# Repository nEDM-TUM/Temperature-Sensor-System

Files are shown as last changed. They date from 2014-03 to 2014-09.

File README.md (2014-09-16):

Temperature-Sensor-System
==============

Sensor network system built for the nEDM experiment.

Features
------------------
- Both temperature and humidity sensors can be connected at any sensor socket.
The sensor type will be automatically detected.
- High temperature and humidity accuracy: Temperature sensors are calibrated to ±0.1K and the humidity sensors to ±1.8%rH.
- A high number of connected sensors is supported. Currently 44 sensors are in use, however the system is designed to support at least 100 sensors and still be able to fulfill a sampling rate of 1Hz. If the sampling rate is allowed to be slower, up to 960 sensors are possible to share one Ethernet connection.
- The system supports a fast sample rate of at least 1Hz.
- We achieved a relatively low cost per sensor. The cost per sensor module is mostly defined by the sensor chip alone, which is about e7 for a precision temperature sensor and about e20 for a high quality humidity sensor. The cost for the printed circuit board and required components is less than e4 per board.
- Measurement results can be forwarded via TCP/IP to a CouchDB server, which is able to record the measurement data from all connected sensors.
- The sensor network provides a TCP/telnet user interface, for controlling and viewing of network parameters. This allows easy configuring and debugging of the system.
- Most of the system parameters like sampling rate or database IP addresses and insert functions are configurable at runtime.
- Plug and Play is supported for adding and removing sensors or even control units during runtime.

Directory structure
--------------------
```
.
+-- casings     // 3D CAD files for 3D printer
|   +-- adapter
|   +-- arduino
|   +-- cable_clamp
|   +-- collector
|   +-- humidity
|   +-- temperature
+-- circuit_boards      // Circuit schematic diagram and 
|   |                   // PCB schematic files created using KiCad
|   +-- 3x127_254_adapter       // A PCB chip adapter, 
|   |                           // used for breadboard debugging
|   +-- 4x127_254_adapter       // A PCB chip adapter, 
|   |                           // used for breadboard debugging
|   +-- arduino_adapter
|   +-- humidity
|   +-- kicad_library           // Footprint and Component
|   |                           // library files for KiCad
|   +-- order           // PCB assembly, which was sent to 
|   |                   // Fischer Leiterplatten for production
|   +-- sensor_board
|   +-- so8_breakout    // A PCB chip adapter, 
|   |                   // used for breadboard debugging
|   +-- temperature_board
+-- datasheets      // Datasheets for sensors, micro processor, etc.
+-- presentation    // Slides (tex files) for a project presentation
+-- registration    
|   +-- description     // Project description (tex files) 
|                       // used for registration
+-- report      // Main project documentation (tex files)
+-- shop_orders // Receipts of orders from hardware shops
+-- sofware
|   +-- avr_wcet_analyzer   // code of a WCET analyzer
|   |                       // for the AVR instruction set
|   +-- collector_board      
|   +-- ethernet_board        
|   +-- humidity_board      
|   +-- util        // Commonly used utility code
+-- squid_analysis      
|   +-- data            // Squid magnetic field measurement protocol.
|                       // For squid data please write a mail to us.
|   +-- evaluation      // Evaluation script of squid analysis data
```

Tips for developers
--------------------
- To prevent EEPROM from being corrupted on power cycles, the AVR integrated brownout detection should be enabled.
- To allow EEPROM storage to stay intact after reprogramming, set the corresponding fuse bit.
- As Arduino fuses are not possible to be programmed via the default Arduino programmer (using the Arduino boot loader), we removed the boot loader and use the ISP connector for programming.
- To not overload the voltage regulator, especially when driving multiple boards one should consider, that a significant portion of power is used to drive LEDs. So turning the LEDs off during normal operation will prevent overheating.
- When debugging and programming devices of the sensor network, one has to be very careful, to not provide different power sources, as this might cause unexpected results, which can lead to damage of the sensor network, as well as connected computers. By default the USBasp programmer provides the system with 5V power.
- Our makefiles currently do not support automatic detection of file dependencies, and source files to be compiled. All source files have to be specified explicitly and if changes to header files are made, a ’make clean’ should be performed before compiling the program.
- Be careful, when using the USART line or similar for generating debugging output. Transmitting debugging information takes relatively long time and might influence the system heavily, especially, when debugging timing critical code. LEDs or GPIO pins with an oscilloscope provide a faster but more complex way for debugging.

###For more details about our project, please read the report document. ###
Its tex file and needed images can be found in the folder _report_. You can use _make_ to compile the document.

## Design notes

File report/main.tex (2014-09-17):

% Cover letter using letter.cls
\documentclass[a4paper]{scrreprt} 
%\usepackage{helvetica} % uses helvetica postscript font (download helvetica.sty)
%\usepackage{newcent}   % uses new century schoolbook postscript font 
\usepackage[utf8]{inputenc}
\usepackage[toc,page]{appendix}
\usepackage{graphicx}
\usepackage{amsmath}
\usepackage{eurosym}
\usepackage{cite}
\usepackage{tabularx}
\usepackage{bytefield}
\usepackage{color}
\usepackage{longtable}
\usepackage{tabularx}
\usepackage{url}
\usepackage[bookmarks]{hyperref}
\hypersetup{pdftex,colorlinks=true,allcolors=black}
\usepackage{hypcap}
\usepackage{listings}
\usepackage{color}
% the following commands control the margins:
%\topmargin=-1in    % Make letterhead start about 1 inch from top of page 
%\textheight=8.5in    % text height can be bigger for a longer letter
%\oddsidemargin=0pt   % leftmargin is 1 inch
%\textwidth=6.5in     % textwidth of 6.5in leaves 1 inch for right margin
\title{Implementing a temperature and humidity sensor network for the nEDM
experiment setup}
\author{Wenwen Chen, Rainer Schönberger}
\begin{document}
\maketitle
\tableofcontents
%###############################################################
\chapter{Introduction}
%%%%%%%%%%%%%%%%%%%%%%%%%%%%%%%%%%%%%%%%%%%%%%%%%%%%%%%%%%%%%%%
\section{Background}
\subsection{The neutron electric dipole measurement}
According to the standard model, it is assumed, that neutrons possess a electric dipole moment (EDM)
in the order of $10^{-32}e\cdot cm$. However an extension of the standard model already predicts
a dipole moment in the order between $10^{-26}e\cdot cm$ and $10^{-28}e\cdot cm$. Until now, no
experiment was able to do measurements more precise than $10^{-26}e\cdot cm$\cite{frmexp}.\\
The Neutron EDM (nEDM) experiment at Technische Universitat München is trying to increase the precision
of such a dipole moment measurement\cite{frmexp}.\\
The experiment uses spin polarized ultra cold neutrons, which are guided into two chambers inside a
highly controlled and magnetically shielded environment (see figure \ref{fig:exp}). There, a spin precession measurement according
to Ramsey \cite{ramsey} is performed, which allows it, to get information about the dipole moment of the neutrons.
\begin{figure}[h]
\centering
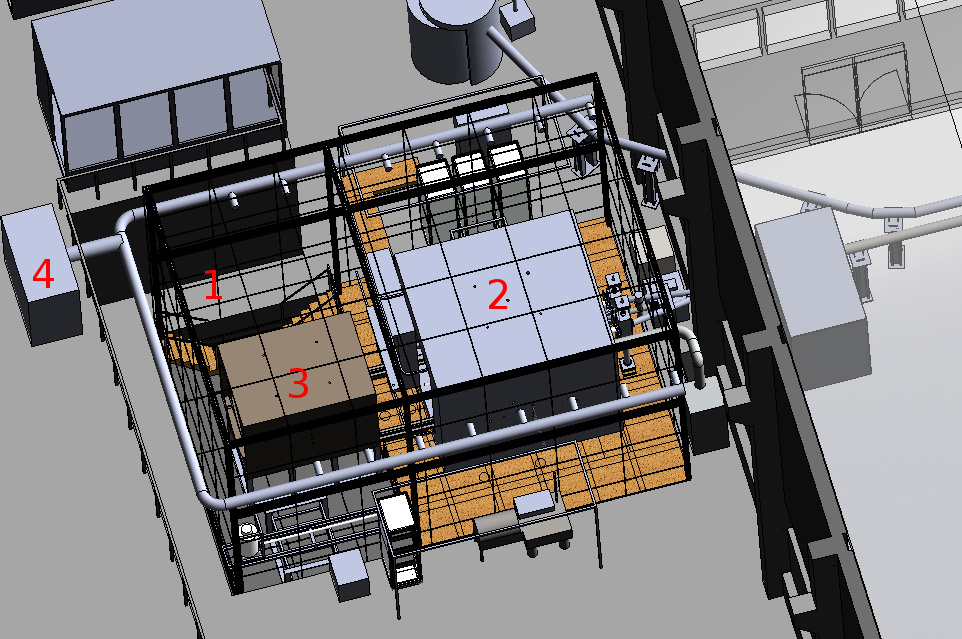
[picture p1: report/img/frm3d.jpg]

\caption{Experiment environment. 1: Field cage for magnetic field compensation, 2: Outer magnetic shield, 3: Inner magnetic shield, 4: Air conditioning system. Source: \cite{fiewiki}}
\label{fig:exp}
\end{figure}
\subsection{Temperature measurement}
Besides an exactly defined magnetic environment inside the experiment setup, a well defined
environment temperature and humidity is also important for the experiment. Therefore a
air conditioning system is installed to regulate the temperature inside the field cage.
Our temperature sensor network will provide data for the air conditioning system.\\
As a precise homogeneous temperature distribution inside the whole field cage is
almost impossible to achieve, our sensor network will provide precise temperature and humidity data. These data can be used to determine if specific physical observations are dependant
on temperature changes in the environment. Also a temperature compensation of measurements
based on environment temperature is possible.
%%%%%%%%%%%%%%%%%%%%%%%%%%%%%%%%%%%%%%%%%%%%%%%%%%%%%%%%%%%%%%%
\section{Features}
Our finished sensor network provides the following features:
\begin{itemize}
  \item Both temperature and humidity sensors can be connected at any
    sensor socket. The sensor type will be automatically detected.
  \item High temperature and humidity accuracy: Temperature sensors
    are calibrated to $\pm 0.1\,\mathrm{K}$ and the humidity
    sensors to $\pm 1.8\,\%\,\mathrm{rH}$.
  \item A high number of connected sensors is supported.
    Currently 44 sensors are in use, however the system is designed
    to support at least 100 sensors and still be able to fulfill a
    sampling rate of $1\,\mathrm{Hz}$. If the sampling rate is
    allowed to be slower, up to 960 sensors are possible to share
    one Ethernet connection.
  \item The system supports a fast sample rate of at least $1\,\mathrm{Hz}$.
  \item We achieved a relatively low cost per sensor. The cost per
    sensor module is mostly
    defined by the sensor chip alone, which is about \EUR{7} for a
    precision temperature sensor and about \EUR{20} for a high quality
    humidity sensor (also see section \ref{chap:sensors}). The cost for
    the printed circuit board and required components is less than
    \EUR{4} per board.
  \item Measurement results can be forwarded via TCP/IP to a CouchDB
    server, which is able to record the measurement data from all
    connected sensors.
  \item The sensor network provides a TCP/telnet user interface, for
    controlling and viewing of network parameters. This allows easy configuring
    and debugging of the system.
  \item Most of the system parameters like sampling rate or database IP addresses
    and insert functions are configurable at runtime.
  \item Plug and Play is supported for adding and removing sensors or even
    control units during runtime.
\end{itemize}
%###############################################################
\chapter{Technology}
%%%%%%%%%%%%%%%%%%%%%%%%%%%%%%%%%%%%%%%%%%%%%%%%%%%%%%%%%%%%%%%
\section{Sensors}\label{chap:sensors}
\subsection{TSIC 506F}
For temperature measurements, we use the TSIC 506F temperature sensor
integrated circuit chip. At a relatively low price of about \EUR{7} per device, it
is able to deliver very high accuracy (see table \ref{tab:tsic}).\\
The temperature is converted to a digital value, which is sent out over a
proprietary one wire protocol variant, called \emph{ZAC-Wire}. The transmission structure can be seen in figure \ref{fig:tsic_transmission}. Details about the ZACwire protocol are described in section \ref{chap:zac}.\\
The temperature $T$ in Celsius can be calculated from the received value $T_{dig}$ using
$$T\,[^{\circ} C] = \frac{T_{dig}}{2047} \cdot 70 - 10$$\\
In order to minimize soldering heat, which would influence the calibration, we used the TO92 packaged sensor.\\
For further information about the sensor, and data interpretation, please refer to \cite{tsic} and \cite{tsic2}.
\begin{table}[Hh!]
	\centering
	\begin{tabular}{| r | c |}
		\hline
		Temperature range & $-10\,^{\circ}\mathrm{C}$ to $60\,^{\circ}\mathrm{C}$\\
		\hline
		Calibrated accuracy & $\pm 0.1\,\mathrm{K}$  \\
		\hline
		Resolution & $0.034\,\mathrm{K}$  \\
		\hline
	\end{tabular}
  \caption{TSIC 506F specification \cite{tsic2}}
	\label{tab:tsic}
\end{table}
\begin{figure}[Hh!]
	\centering
	\definecolor{lightgray}{gray}{0.8}
	\begin{bytefield}[endianness=big, bitwidth=2.1em]{10}
		\bitheader{0-9}\\
    \bitbox{1}{ST} & \bitbox{5}{0} & \bitbox{3}{$T_{dig}$[10:8]} & \bitbox{1}{P}\\
    \bitbox{1}{ST} & \bitbox{8}{$T_{dig}$[7:0]} & \bitbox{1}{P}
	\end{bytefield}
  \caption{TSIC transmission structure. The temperature is sent over the wire, with two ZACwire transmissions. P is an even parity bit. ST is the start bit \cite{tsic}.}
	\label{fig:tsic_transmission}
\end{figure}
\subsection{HYT271}
\label{sec:sensor_hyt281}
For humidity measurement, we use the HYT271 sensor. At a price of about \EUR{20} per device it is significantly more expensive than the temperature sensors, however it delivers precise and temperature compensated humidity measurements. 
The humidity value rH in percent can simply be calculated from the received value $\mathrm{rH}_{dig}$ using
$$\mathrm{rH}\,[\%] = \frac{100}{2^{14}} \cdot  \mathrm{rH}_{dig}$$\\
In addition, the temperature can also be read out and calculate using 
$$T\,[^{\circ} C] = \frac{165}{2^{14}} \cdot  T_{dig} - 40$$\\
Table \ref{tab:hyt} lists the specified sensor characteristics.
\begin{table}[Hh!]
	\centering
	\begin{tabular}{| r | c | c |}
		\hline
    &Temperature & Humidity\\
		\hline
		\hline
    Range & $-40\,^{\circ}\mathrm{C}$ to $125\,^{\circ}\mathrm{C}$ & $0\, \mathrm {\%rH}$ to $100\, \mathrm {\%rH}$\\
		\hline
    Calibrated accuracy & $\pm 0.2\,\mathrm{K}$ & $\pm 1.8\, \mathrm {\%rH}$   \\
		\hline
    Resolution & $0.015\,\mathrm{K}$ & $\pm 0.03\, \mathrm {\%rH}$ \\
		\hline
	\end{tabular}
  \caption{HYT271 specification \cite{hyt}}
	\label{tab:hyt}
\end{table}\\
Communication with the sensor is done via I2C. Thereby measurements can be initialized via addressing the sensor and sending a write bit. The result of a measurement can be received by initializing an I2C read transfer, followed by reading the measurement data. Figure \ref{fig:hyt_transmission} shows the format of received measurement data. The second status bit, the stale bit, sent at the beginning, gives information, whether a new measured value is ready after the last readout. The reception of data may be aborted, by the I2C master after every byte, if not all data is needed.
\begin{figure}[Hh!]
	\centering
	\definecolor{lightgray}{gray}{0.8}
	\begin{bytefield}[endianness=big, bitwidth=2.1em]{8}
		\bitheader{0-7}\\
    \bitbox{2}{Status} & \bitbox[lrt]{6}{}\\
    \wordbox[lrb]{1}{Humidity}\\
    \bitbox{2}{\color{lightgray}\rule{\width}{\height}} & \bitbox[lrt]{6}{}\\
    \wordbox[lrb]{1}{Temperature}\\
	\end{bytefield}
  \caption{HYT271 transmission structure. The humidity value and temperature value each consist of 14 bits. The two bits, marked with gray color, before the temperature value are undefined \cite{hyt2}.}
	\label{fig:hyt_transmission}
\end{figure}\\
For further information about the sensor, and data interpretation, please refer to \cite{hyt}, \cite{hyt3} and \cite{hyt2}.
%%%%%%%%%%%%%%%%%%%%%%%%%%%%%%%%%%%%%%%%%%%%%%%%%%%%%%%%%%%%%%%
\section{Protocols}
In this section, the mainly used low level protocols for measuring and data forwarding will be introduced shortly. 
\subsection{ZACwire}\label{chap:zac}
ZACwire is a proprietary one wire communication protocol, developed
by IST AG. ``One wire'' means that only one data line is needed.\\
Each bit is represented by
different duty cycles of the waveform within the bit time $T_b$.
Every normal bit starts with a falling edge. At the beginning
of each transmission, a start bit with a duty cycle of 50\% is
transmitted. From this start bit, the bit time $T_b$ for the
transmission can be extracted. 
If the bus is 75\% high within the bit time $T_b$ the bit `1' is transfered, otherwise bit `0'. 
If the bus is high for a time $>T_b$
the transmission ends, this is called a Stop bit. Figure \ref{fig:zac}
shows the four different waveform types, of which a ZACwire signal can be
composed. Figure \ref{fig:zacexample} shows an example
transmission. For further information see \cite{zac}.
\begin{figure}[Hh!]
	\centering
	
	\caption{ZACwire protocol signal interpretation}
	\label{fig:zac}
\end{figure}
\begin{figure}[h]
	\centering
	
	\caption{ZACwire protocol example}
	\label{fig:zacexample}
\end{figure}
\subsection{I2C}
I2C is a bus protocol, which specifies the physical layer, as well as an arbitration and addressing layer. The protocol is a two wire protocol and allows communication between multiple bus participants.\\
Transmissions are done over two transmission lines SCL and SDA, which
are pulled to logical high voltage level by pull up resistors (see
figure \ref{fig:i2c}). Each transmission is controlled by a device
in master mode, which provides a clock by controlling the SCL line.\\
A transmission is surrounded by a START and a STOP bit, which are code violations.\\
At the beginning of a transmission, the master first transmits an
address to the bus, addressing one or all connected devices which
are in slave mode. After that a data direction bit is sent to the
bus, which defines the slave behavior: read or write. If the direction bit specifies a write, all addressed slave devices read bits from the bus at every 
clock cycle, the SDA line stays under control of the master. If the
direction bit describes a read, the slave should take control over
the SDA line and transmits bits at every clock cycle.\\
The Slave is allowed to take control over the SCL line at any time
by pulling it low. This is called clock extension, and signals the
master to not proceed transmitting or receiving data.
The full I2C specification can be found in \cite{i2c}.
\begin{figure}[Hh!]
	\centering
	
  \caption{I2C logical bus structure. Source \cite{i2c}.}
	\label{fig:i2c}
\end{figure}
\subsection{RS485}
RS485 is a transmission line standard, which specifies differential line communication over twisted pair cables.
It allows very long distance communication of up to 1 kilometer with high noise immunity and reduced noise emission.\\
Figure \ref{fig:rs485} illustrates the working principle of the protocol.
The encoder transforms a single bit line DI into two separate lines A and B.
If DI is high, the output voltage at line A ($V_{OA}$) will be bigger than at line B ($V_{OB}$).
If the input voltage at DI is low, $V_{OB}>V_{OA}$ holds.\\
A detailed description of the protocol and its implementation can be found in \cite{rs485}, \cite{st485} and \cite{st485appnote}.
\null
\vfill
\begin{figure}[htbp]
	\centering
	
  \caption{RS485 encoding/decoding - Logical structure. Source: \cite{rs485}.}
	\label{fig:rs485}
\end{figure}
%%%%%%%%%%%%%%%%%%%%%%%%%%%%%%%%%%%%%%%%%%%%%%%%%%%%%%%%%%%%%%%
\section{Toolchain}
\subsection{KiCad}
To design schematic circuit diagrams, as well as printed multilayer circuit boards, we used the open source EDA suite KiCad\footnote{http://www.kicad-pcb.org}. Most of the schematic and footprint components, were designed by ourselves and can be found in the project git repository.\\
The finished board files were exported to the Gerber / Echelon file format and sent to Fischer Leiterplatten\footnote{http://www.fischer-leiterplatten.de} for production.
\subsection{ISP programming}\label{chap:isp}
To upload the compiled code and to configure the microprocessors, we used the USBasp programmer in combination with the avrdude software.\\
As we needed to access the fuse bytes of the Arduino too, which was not possible with the Arduino bootloader, we also use the ISP header on the Arduino board for programming. The Arduino boot loader was removed. Hence it is not possible anymore, to program the Arduino with the Arduino software suite, without reinstalling the boot loader.\\
\textbf{Note} that the Arduino ISP header is not compatible with the one, provided by the USBasp programmer. A mechanical adapter or individual cabling is required. 
Figure \ref{fig:isp} shows the pin assignments of the different ISP headers.
\begin{figure}[htbp]
	\centering
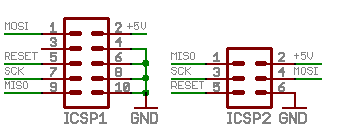
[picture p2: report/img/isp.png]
	
  \caption{ISP connector pin assignments. Left: 10 pin version (used by USBasp, and on our boards), right: 6 pin version (as used on arduino boards). Source: \cite{micronet}.}
	\label{fig:isp}
\end{figure}
\subsection{USART for debugging}
For convenient debugging, we added a USART header on each board with a micro controller. 
These pins are directly connected to the hardware USART unit of the micro controller.\\ 
\textbf{Note} that the signal level on this header is TTL and is not compatible with the RS232 standard. It is possible to connect the boards to a PC, using either an external signal level converter from TTL to RS232, or a direct USB to USART TTL converter.\\
In every software component, we set the \emph{stdout} file descriptor, to point to a USART file, implementing writing data to the USART line.
Hence standard file handling functions like \emph{printf} or \emph{puts} can be used for printing debugging information.\\
To read and write data at the PC side, software like \emph{screen} or \emph{picocom} may be used. The default baud rate is 9600bps.
\subsection{Build process}
To build and upload the code the following software and libraries are required:\\
Tools:
\begin{itemize}
  \item avr-gcc
  \item avr-objcopy
  \item avrdude or other ISP programming software
\end{itemize}
Libraries:
\begin{itemize}
  \item avr-libc
  \item Arduino ethernet library (only for Ethernet board)
  \item Arduino core library (only for Ethernet board)
\end{itemize}
We use the make build environment. The Makefiles in each software directory contain instructions on how to build and upload the software to the micro controller, using the following rules:
\begin{description}
  \item[make clean] Clears the build directory.
  \item[make] Compiles and links the source code to the elf and Intel hex binary format. Also a EEPROM image is generated in Intel hex binary format. The output directory for binary files will be \emph{./build/}.
  \item[make fuse] Configures the controller, to use the right system clock source, burnout detection and EEPROM persistency settings.
  \item[make eeprom] Uploads the EEPROM image to the controller.
  \item[make upload] Uploads the compiled software to the micro controller, using avrdude. By default the usbasp programmer is selected.
\end{description}
For a first time build and upload, the above order should be respected. After the initial upload, fuses and EEPROM should not be touched every time, the software changes.\\
To be able to find the Arduino library root path, the \emph{ARDUINO\_PATH} environment variable should be set to the Arduino installation directory. This for example is the path to the cloned Arduino git repository.\\
\textbf{Note}, that the Makefiles in the current version, do not automatically search for file dependencies, hence a make clean should be executed, after every change in not explicitly specified files, namely every non .c or .cpp file.

%###############################################################
\chapter{Implementation}
%%%%%%%%%%%%%%%%%%%%%%%%%%%%%%%%%%%%%%%%%%%%%%%%%%%%%%%%%%%%%%%
\section{Logical design}
Our network architecture is structured into 3 parts (see figure \ref{fig:topo}).
For each part, we developed a different kind of device. The job of each part
is described in the following:
\begin{figure}[Hh!]
	\centering
	
	\caption{Network topology, showing the different devices in the network.}
	\label{fig:topo}
\end{figure}
\begin{description}
  \item[Measuring]\hfill \\
    Sensors do periodic measurements. The results are transmitted,
    using an unified protocol. We used ZACwire, as the unified
    protocol, as in our application we have more temperature sensors,
    which natively speak ZACwire, than humidity sensors. Hence no
    protocol conversion will be required for the majority of the
    sensor boards. 
    Using RS485 as a physical layer protocol, the range of the
    ZACwire signal has been extended with a improved noise behavior.
  \item[Data acquisition]\hfill \\
    At this part of the network, the ZACwire signal from the sensors
    is interpreted and buffered. The measurement data is then
    provided over an I2C interface.\\
    In our implementation, we support sampling of up to 8 Sensors
    per collector board. To increase the numbers of sensors in the
    network, multiple collector boards may be connected to the I2C
    bus, using the I2C chaining connectors. With this technique,
    the network theoretically may consist of up to
    $120\cdot 8 = 960$ sensors\footnote{Eight I2C addresses are reserved}.
  \item[Data forwarding]\hfill \\
    The forwarding part controls the data acquisition part of the
    network and provides an interface to IP networks. Data can be
    forwarded to a couchDB database on the internet. Furthermore, the network 
    is configurable via an telnet/netcat terminal user interface.
\end{description}
%%%%%%%%%%%%%%%%%%%%%%%%%%%%%%%%%%%%%%%%%%%%%%%%%%%%%%%%%%%%%%%
\section{Sensor boards} \label{chap:sensorbrd}
\subsection{Temperature board} \label{chap:tempbrd}
The temperature board consists of the TSic506F sensor and
complementary circuitry. The ZACwire signal is transformed to the
RS485 electrical layer, using a ST485 integrated circuit. The board
provides a RJ45 socket,  over which the required supply voltage of 5V
should be provided, and the two differential signal outputs can be
received. The schematic diagram can be seen in figure
\ref{fig:schem_temp}.\\
Care was taken, when soldering the temperature sensor, to minimize
heat transfer to the chip. We did this by soldering each pin for a
maximum time of 2 seconds, We also tried to keep the total time spent
for soldering all 3 pins less than 10 seconds. After soldering, we
immediately blew cold air to the pins and the chip itself.\\
Figure \ref{fig:pcb_temp} shows the printed circuit board (PCB) schematic
and figure \ref{fig:soldered_temp} the not completely soldered
temperature board. 
In order to reduce the influence of heat from the other electronic
components, the temperature sensor is placed far away from the others
and PCB the traces to the temperature sensor are thin and guided through
a narrow neck.
\subsection{Humidity board}
The hardware structure is similar to the temperature board, described in section \ref{chap:tempbrd}. However, as the HYT271 sensors use I2C for
communication, we added a micro controller to repeatedly poll the sensor for current measurement results and send the data out using a software
implementation of the ZAC wire protocol. Therefore we also placed an ISP socket, a debugging adapter, a reset switch and two LEDs onto the board, which makes it
slightly bigger than the temperature board. The schematic can be seen in figure \ref{fig:schem_hum}.\\
The design of the PCB (see figure \ref{fig:pcb_hum}) is also similar to the temperature board. 
\subsubsection{ZAC encoding}
The most easy method to generate a ZAC encoded signal is to set a pin high, then use busy-wait delay loop (\texttt{\_delay\_us()}) to wait a certain time interval. After that set the pin to low. 
But the timing of this method is not very exact (more than 6 $\mu s$ inaccuracy according to experience). Hence we decided to use a timer to achieve a higher timing accuracy. \\
We have used the following timer features, which are triggered on compare match: 
\begin{itemize}
  \item Clear timer, when the timer counter matches the output compare register value. This is the so called ``CTC mode'' of the timer.
  \item Toggle an output pin if a compare match occurs. It will be also possible to explicitly set the pin high or low.
  \item Execute an interrupt handler on compare match. This allows us to change the value of the output compare register on demand.
\end{itemize}
Figure \ref{fig:zac_encoding} shows an example of the ZACwire signal encoding process.\\
\begin{figure}[Hh!]
	\centering
	
	\caption{ZACwire signal encoding processing example.}
	\label{fig:zac_encoding}
\end{figure}
We keep the output pin high, when there is nothing to do.
If a measured value is ready to be sent, the timer will be configured to enable the above described features and the output compare register will be set to half of the defined bit time for sending a start bit.
After that, the output compare register will be set to $\frac{T_{b}}{4}$ or $\frac{3}{4}T_{b}$ according to the sending bit.
After the last bit is sent, the output pin will stay high, which indicates a stop bit. 
When a newly measured value is ready again, the whole procedure will be executed again.
\\
For detailed usage description of the microprocessor timer, please read the corresponding data sheet. For the microprocessor ATmega88P, which we used, see \cite{atmega88}.\\
\subsubsection{Cyclic redundancy check (CRC)}\label{chap:crc}
In order to detect errors after a long distance transmission, 
We attach an 8-bit CRC checksum for every block of measured values before sending the data out. \\
CRC is a common method for error-detecting in digital networks and is based on the theory of polynomial division. 
In the Galois field of two elements, GF(2),
an n-bit checksum is the remainder of the division between data, shifted n bit to the left, and a (n+1)-bit polynomial as the divisor.
Because the polynomial division in GF(2) is equivalent to an iteration of the bitwise XOR, a checksum can be computed in the following way:
The divisor is at first shifted to the leftmost side of the input data block and computed XOR with the first (n+1) bits.
Then the rest of the unchanged input is appended to the result and becomes the new input to do the same XOR calculation with the divisor again.
If the result is zero, the divisor will be shifted to the first bit `1' and XORed with the (n+1) bits, starting with the bit `1'. 
The XOR calculation will be repeated until no rest bits exist to attach and the n bits remainder then is the wanted CRC checksum.
An example of the calculation of a 4-bit checksum to the polynomial divisor 10011 (0x13) using this algorithm will be shown below:
\definecolor{backcolour}{rgb}{0.95,0.95,0.92}

\lstdefinestyle{mathstyle}{
    backgroundcolor=\color{backcolour},   
    basicstyle=\scriptsize\ttfamily,
    breakatwhitespace=false,         
    breaklines=true,                 
    captionpos=b,                    
    keepspaces=false,                                 
    showspaces=false,                
    showstringspaces=false,
    showtabs=false,                  
    tabsize=2
}
\lstset{style=mathstyle}
\begin{lstlisting}[xleftmargin=25pt, xrightmargin=25pt,framexleftmargin=10pt,framextopmargin=10pt, framexbottommargin=10pt]
1101 1001 1010 0011 0000  <-- input data block, shifted 4 bits to left 
1001 1                    <-- polynomial divisor
------------------------
 100 0001 0100 0011 0000  <-- result of the first XOR round
 100 11
 -----------------------
     1101 0100 0011 0000
     1001 1
     -------------------
      100 1100 0011 0000
      100 11
      ------------------
                 11 0000
                 10 011
                 -------
                  1 0110
                  1 0011
                  ------
                     101 <---remainder, the checksum
\end{lstlisting}
For checking the correctness of received data, the division of received data and the same polynomial is repeated.
If the remainder is not equal zero, some error of the transfered data is detected, otherwise no error is found.
But that does not mean, no error exists.
It might happen, that the change of some bits accidentally leads to a zero remainder. However, the probability of such detectable error is very low.\\
The polynomial, which we use, is the standard CRC-8 for 1-wire bus systems: 100110001(0x131).
\subsubsection{Transmission structure}
After having fetched a block of valid measurement values, whose stale bit is zero (see section \ref{sec:sensor_hyt281}),
the status bits will be removed.
Then a CRC-8 checksum will be computed and attached after the data block.
After that, the whole data will be encoded to ZACwire signals and sent out.
Figure \ref{fig:hyt_board_transmission} shows the new transmission structure, of the ZACwire transmission.
\begin{figure}[Hh!]
	\centering
	\definecolor{lightgray}{gray}{0.8}
	\begin{bytefield}[endianness=big, bitwidth=2.1em]{8}
		\bitheader{0-7}\\
    \bitbox[b]{7}{} & \bitbox{1}{ST}\\
    \bitbox{2}{0} & \bitbox[lrt]{6}{}\\
    \wordbox[lrb]{1}{Humidity}\\
    \bitbox{2}{\color{lightgray}\rule{\width}{\height}} & \bitbox[lrt]{6}{}\\
    \wordbox[lrb]{1}{Temperature}\\
    \bitbox{8}{CRC-8}
	\end{bytefield}
  \caption{ZACwire Transmission structure of data, which is sent out from the humidity board. The two bits, marked with gray color, before the temperature value are undefined. ST represents the start bit.}
	\label{fig:hyt_board_transmission}
\end{figure}\\
%%%%%%%%%%%%%%%%%%%%%%%%%%%%%%%%%%%%%%%%%%%%%%%%%%%%%%%%%%%%%%%
\section{Collector board}
The collector board decodes the ZAC protocol and provides an I2C interface
for users, to read out temperature, as well as humidity values of connected sensors.
Care was taken, to ensure a response time of $<1\,\mathrm{s}$.
\subsection{Hardware}
The schematic diagram can be seen in figure \ref{fig:schem_collect}. The hardware consists of the following main components:
\begin{description}
  \item[Microprocessor:]\hspace{1cm}\\
    To do all protocol conversion tasks, we used an Atmel Atmega88PA
    micro controller, running at a clock speed of $20MHz$. The clock
    is generated, using an external crystal oscillator.\\
    The Atmega micro controller provides a variety of useful features
    like asynchronous timers, pin change interrupts on every GPIO (General Purpose Input/Output)
    pin, hardware support for the I2C protocol and integrated EEPROM
    storage (Data sheet: \cite{atmega88}).\\
    We connected the sensors in two groups, so that we are able to
    receive two independent interrupts for two sensors in different
    groups.
  \item[I2C connection:]\hspace{1cm}\\
    The board provides two 6-pin I2C pin headers (P3 and P4 of the schematic diagram in figure \ref{fig:schem_collect}), which
    provide connection to the I2C bus, as well as an optional 5V
    power line (Vi2c). The two headers are connected in parallel,
    so they can be used for chaining multiple collector boards.\\
    The board also has integrated I2C pull ups, which can be enabled
    using the switch SW2 (see figure \ref{fig:schem_collect}), in case the I2C master does not provide
    pull ups.
  \item[Sensor connection:]\hspace{1cm}\\
    The individual sensors are connected via an eight-port RJ45
    socket header. Shielding of the RJ45 sockets is connected to
    board ground. The signal of each sensor is first interpreted
    by an RS485 transceiver and afterwards directly provided to a
    micro controller GPIO pin. As this is the receiving side, we also
    had do add impedance matching circuitry. We chose to implement
    a power saving AC-termination solution, as suggested in \cite{st485appnote, rs485}.
    To bring the output level of each transceiver to a defined state,
    when no sensor is connected, we use pull up resistors on the
    input side. Optionally the board and shield ground can be wired to
    the screw pad P2 (see figure \ref{fig:schem_collect}) for a connection with the casing. This is done by
    placing the 0 Ohm resistor R34.
  \item[Developer interface:]\hspace{1cm}\\
    The micro controller can be programmed with any AVR In System
    Programmer, using the standard ISP header (P8 in figure \ref{fig:schem_collect}).\\
    For debugging code, we also added a USART pin header (P1 in figure \ref{fig:schem_collect}), which
    allows serial communication with the micro controller. 
    \\
    \textbf{Note}, when connecting the chip to a PC, as the logic
    levels of our board are 5V TLL and hence are not compatible
    with the RS-232 logic levels, used by most PCs. We suggest to use
    a USB to USART TLL converter or a logic level converter.
  \item[Power source:]\hspace{1cm}\\
    We provide multiple ways to supply power to the collector board.
    \begin{itemize}
      \item Direct 5V input/output (P7 or P9 in figure \ref{fig:schem_collect})
      \item Use the 5V supply voltage, provided via the I2C bus
      \item Unregulated input (7V..25V). The on-board LM7805 linear
        regulator, will convert the voltage to 5V.
    \end{itemize}
    Using the pin header K1, which is marked in figure \ref{fig:schem_collect}, it is possible to select suitable
    power inputs.\\
    Example 1: If the board should get power over I2C, pins 1 and 2
    should be shorted.\\
    Example 2: If the board should get power from the on board
    regulator, and also provide power to the I2C bus, all three pins
    should be shorted.
\end{description}
Figure \ref{fig:pcb_collector} shows the printed circuit board (PCB) schema and figure \ref{fig:soldered_col} a soldered collector board.
\subsection{ZAC decoding}
AVR controllers do not have hardware support for decoding the ZAC one wire
protocol (protocol definition is explained in chapter \ref{chap:zac}). Hence we
implemented a software decoder. However our implementation
does not follow the method suggested by \cite{zac} because of timing reasons.\\
To decode one ZAC protocol sensor, we use the pin change interrupt (PCINT) of the pin, connected to the sensor, and
one 8 bit timer with the corresponding timer overflow interrupt.
\paragraph{Pin change Interrupt:} On every pin change interrupt, the following actions are executed:\\
Every time:
\begin{itemize}
	\item The current time value is stored to a temporary variable $T_{timer}$, to be able to still access it later.
	\item The timer is reset.
	\item If the timer is not jet running, it is started now.
\end{itemize}
On a falling edge:
\begin{itemize}
	\item If $\left|T_{low} - T_{timer}\right| < T_{thresh}$ with a constant $T_{thresh} << T_{crit}$, we
		have observed a start bit.\\
		We now update the critical sampling time\footnote{$T_{crit} = 0.5\cdot(T_{timer} + T_{low})$ would
		be more accurate, but would consume more time to calculate.}: $T_{crit} = T_{timer}$.
    The critical sampling time, is the time, we will wait in the future, after seeing a falling edge, to determine the bit value.
\end{itemize}
On a rising edge:
\begin{itemize}
	\item The current timer value is stored as $T_{low}$. If we already observed a falling edge, this
		represents the time, the signal was low.
	\item If we already have seen a start bit, we now sample a data bit\footnote{Note, that a repeated
		start bit would also be sampled as a data bit with an unpredictable value.}:\\
	$\mathrm{bit} = \begin{cases} 1 & \text{if } T_{timer}<T_{crit} \\ 0 & \text{else}\end{cases}$
\end{itemize}
\paragraph{Timer overflow Interrupt:} The timer is configured in a way, that an overflow will occur after
the timer is running without a reset for $T_{ovf}$, with $T_{bit} < T_{ovf} < 100\,\mathrm{ms}$. Hence
the interrupt will occur, after a completed transmission and before the start of the next transmission.\\
After a overflow occurs, we check, if we received a whole transmission.
This is done, by filling the receive buffer with all ones prior to receiving. Then we use the fact, that
the TSIC sensor, as well as the humidity board start the transmission with a 0 bit (see figure \ref{fig:tsic_transmission} and \ref{fig:hyt_board_transmission}.
Hence, if we see a
0 on the expected position of a humidity readout or a TSIC readout after a timeout, we might have
enough data and stop the sampling, as the transmission is most likely complete.\\
Sampling is stopped by disabling the
interrupts. However, if we did not receive enough data, we reset the receive buffer and wait for the
next transmission to begin.\\
As the transmission of a humidity board is longer than that of a TSIC sensor, we later will be able to determine the
type of the sensor, by looking at the leftmost bit in the receive buffer, where the first 0 bit of the humidity
board should be. If this bit is 0, we know, that the sample is from a humidity board, else it is from a TSIC
sensor.
%\paragraph{Starting a measurement:} 
\\[0.6cm]
At the beginning of each measuring process, the following is executed:
\begin{itemize}
	\item $T_{crit}$ is set to the maximum value.
	\item $T_{low}$ is set to the minimum value. This will ensure, that we do not
		accidentally recognize the first falling edge as a start bit.
	\item The receive buffer is reset.
	\item Interrupts are enabled.
\end{itemize}
%\paragraph{}
Our algorithm is not able to see stop bits correctly, if $T_{ovf}$ is configured badly.
However in our case we deliberately configured $T_{ovf}$ to be bigger that the maximum
high time in case of a stop bit.
This allows us to only see the end of the complete transmission, as a TSIC sensor also
sends an useless stop bit after the first 9 bits.\\
%\paragraph{}
As we have up to 8 sensors connected to the Atmega88, we have to do one measurement after another.
As one sample of a measurement takes $>100\,\mathrm{ms}$ we would run
into problems reaching the desired sampling rate of $>1\,\mathrm{Hz}$.
Our approach is to sample two sensors at the
same time, using a second 8 bit timer. Our interrupt handler for the ZAC protocol decoding are not interruptible.
Hence, incoming interrupts are delayed for the runtime $t_e$ of currently executed interrupts.
If we have interrupts active for two sensors at the same time, the controller might see a delayed signal.
Figure \ref{fig:zactiming} illustrates this problem:
\begin{figure}[Hh!]
	\centering
	
	\caption{ZAC protocol worst case timing. The grey shaded areas illustrate the potentially delayed vision
	of a micro controller due to interrupt latency.}
	\label{fig:zactiming}
\end{figure}
\\
When sampling the start bit we get an error for our critical time $T_{crit}$:
$$T_{min} := T_h - t_e < T_{crit} < T_h + t_e$$
When using $T_{crit}$ to determine a bit value, we are again influenced by the possibly delayed preceding falling edge. We get:
$$T_{min} < T_{crit}' < T_h + 2 \cdot t_e =: T_{max}$$
In other words, $T_{min}$ is the time, starting from a real falling edge,
before which the controller will not sample the bit. $T_{max}$ is the time,
starting from a real falling edge, after which the controller will not sample
the bit anymore.\\
In order to reliably detect 1s and 0s, our algorithm will only work correctly, if
$$T_{min} > 0.5\cdot T_h + t_e$$
or
$$T_{max} < \frac{3}{2}\cdot T_h\text{.}$$
Both inequations simplify to
$$t_e < \frac{1}{4}\cdot T_h\text{.}$$
According to \cite{zac}, the nominal value for $T_h$ is $\frac{125}{2}\,\mu\mathrm{s}$. Hence our error due to
interrupt latency has to be smaller than $15.625\,\mu\mathrm{s}$.\\
As the micro controller runs at a clock speed of $20\,\mathrm{MHz}$, we have to complete previous interrupts,
start the interrupt handler of the new interrupt and sample the current timer value within 332 clock cycles,
to not harm the above limit on the error.\\
We implemented a simple branch aware Worst Case Execution Time (WCET) analyzer for the AVR instruction set.
It is able to calculate the maximum execution time of individual sections in the compiled code\footnote{\textbf{Note} that,
whereas branches are considered, only branches to addresses in the future are handled correctly. Loops i.e.
branches to already executed code cause undefined, possibly non terminating behaviour of the analyzer. As our code
does not contain loops, this did not cause problems and loop handling was not implemented.}. Figure \ref{fig:wcet}
shows the WCET analyzer output for the Pin change interrupt handler. The worst case execution time for the total
handler is $100$ cycles. The timer interrupt handler takes less than $50$ cycles to complete. For a complete analysis one
additionally has to consider the time for jumping to the interrupt handler ($<20$ cycles) and the time we need to read out the
timer value in the new interrupt handler ($<29$ cycles). This gives us a total latency of less than $199$ clock
cycles, which is well within the allowed range.
\begin{figure}
	\centering
	
  \caption{Branch aware WCET analysis of the Interrupt handler for vector\_4 (Pin change interrupt).
  Nodes represent program addresses, arrows represent branches. Red arrows point to the branch with the
highest execution time. The values near the arrows represent the execution time from the previous node's
address to the instruction causing the branch.}
	\label{fig:wcet}
\end{figure}
\subsection{I2C interface}
Communication with the collector board is done via I2C (Two Wire Interface). Thereby the board acts as an
I2C slave, extending the clock, if it is currently not able to process incoming data.
This is especially used while a measurement is in progress: As soon as new data byte arrives,
it is buffered by hardware, without interrupting the measurement and the clock will be extended, signalling to the master, that no further data should be sent or received.\\
If a write request (SLA+W) is sent, the data following the write request is interpreted as a command. A list of implemented commands is given
in table \ref{tab:i2c}. The collector boards react to the general call address 0. This makes it possible to trigger a measurement
on multiple boards, using only one I2C transmission.
Also the I2C address of a collector board can be set to a new value without knowing the old one, when only this board is connected
to the bus and the address 0 is specified as the old address when issuing the address change command.\\
If a read request (SLA+R) is sent, the packet array from the last completed measurement will be sent out, starting with sensor 0.
For details about the packet format see chapter \ref{chap:packet}. Not all packets have to be received, as soon as a STOP bit is
received, the transmission is aborted. A new read request will again trigger the transmission of data starting at sensor 0.
\begin{table}[Hh!]
	\centering
	\begin{tabularx}{\textwidth}{ | c | c | c | X | }
		\hline
    Name & Value & Parameters & Action\\
		\hline
		\hline
    START\_MEASUREMENT & 0x01 & --- & All 8 sensor values will be
    captured as soon as the STOP bit is received. If during
    measurement
		the slave is addressed again, the I2C clock will immediately be extended until the measurement is complete, blocking the whole I2C bus.\\
		\hline
    SET\_ADDRESS & 0x02 & address & The own I2C address will be updated with the 1 byte value following the command. The address should
		be in the range from 8 to 120. The default address is 42\\
		\hline
    LED\_ON & 0x03 & number & The LED with the given number will be turned on.\\
		\hline
    LED\_OFF & 0x04 & number & The LED with the given number will be turned off.\\
		\hline
	\end{tabularx}
	\caption{List of implemented I2C commands}
	\label{tab:i2c}
\end{table}
\subsection{Measurement packet format}\label{chap:packet}
After data was received via the ZAC-Wire protocol, it is interpreted and converted to a convenient packet format, suitable for
redirection via I2C. Figure \ref{fig:packet} shows the structure of a packet.
Each packet's integrity is protected by a CRC checksum (algorithm description see section \ref{chap:crc}) and consists of the following fields:\\
\begin{description}
	\item[\textbf{type}] \hfill\\
        This field specifies the type of the sensor, which supplied the data. Currently implemented values are 0
		for TSIC and 1 for HYT. In case the type field reads 0, the \emph{Humidity} field will have no relevant value and hence
		represents a padding field.
	\item[c] \hfill\\
This bit is set to 1, if the measurement was completed without a timeout. This is usually the case, when a
		sensor is connected. Hence this bit can be used to determine, whether a sensor is connected or not.
	\item[error] \hfill\\
This field reads 1, when an error during sampling has occurred. Possible causes are: HYT Checksum mismatch,
		TSIC Parity mismatch or TSIC Protocol format error.
	\item[Temperature] \hfill\\
$T_m \cdot 100$ with $T_m$ the measured temperature in Celsius.
	\item[Humidity] \hfill\\
$rH_m \cdot 100$ with $rH_m$ the measured relative humidity in \%.
	\item[CRC-8] \hfill\\
Checksum over the first 5 bytes of the packet\footnote{The Humidity field is always part of the checksum
		calculation, even if the packet type is 0.}.
\end{description}
Packets can be received via I2C in the order, shown in
figure \ref{fig:packetorder}.\\
\begin{figure}[Hh!]
	\centering
	\definecolor{lightgray}{gray}{0.8}
	\begin{bytefield}[endianness=big, bitwidth=2.1em]{8}
		\bitheader{0-7}\\
		\begin{rightwordgroup}{Header}
			\bitbox{2}{type} & \bitbox{3}{\color{lightgray}\rule{\width}{\height}} & \bitbox{1}{c} & \bitbox{2}{error}
		\end{rightwordgroup}\\
		\begin{rightwordgroup}{Payload}
			\wordbox{2}{Temperature}\\
			\wordbox{2}{Humidity}
		\end{rightwordgroup}\\
		\wordbox{1}{CRC-8}
	\end{bytefield}
  \caption{Packet format of a measurement. The whole packet is 6 bytes long}
	\label{fig:packet}
\end{figure}
\begin{figure}[Hh!]
	\centering
	\definecolor{lightgray}{gray}{0.8}
	\begin{bytefield}[endianness=little, bitwidth=0.7em]{48}
		\bitheader{0,6,12,18,24,30,36,42}\\
		\bitbox{6}{Sensor 0} &
		\bitbox{6}{Sensor 1} &
		\bitbox{6}{Sensor 2} &
		\bitbox{6}{Sensor 3} &
		\bitbox{6}{Sensor 4} &
		\bitbox{6}{Sensor 5} &
		\bitbox{6}{Sensor 6} &
		\bitbox{6}{Sensor 7}
	\end{bytefield}
  \caption{Transmission packet order}
	\label{fig:packetorder}
\end{figure}

%%%%%%%%%%%%%%%%%%%%%%%%%%%%%%%%%%%%%%%%%%%%%%%%%%%%%%%%%%%%%%%
\section{Ethernet board}
\subsection{Hardware}
For the Ethernet board we use a pre built 
Arduino Ethernet board\footnote{http://arduino.cc/en/Main/ArduinoBoardEthernet},
equipped with a Power over Ethernet module.
The board features an atmega328 micro controller,
which has 32 KByte Flash and 2 KByte RAM storage \cite{atmega328}. The atmega328
controller is connected to a W5100 Ethernet controller and PHY with integrated
TCP/IP stack.\\
As the I/O Pin headers of the Arduino board were not suitable to
use for a reliable connection with the collector boards, we designed an adapter
board, which provides sockets for I2C and power connections. The adapter also
provides I2C pull up resistors and a LED for debugging.
Hence, when using it,
the optional pull up resistors on the collector boards can be switched off.\\
The PCB schematic of the adapter can be found in figure	\ref{fig:pcb_arduino}.
\subsection{Software}
On the software side, the Ethernet board has the following requirements:
\begin{itemize}
  \item Periodically poll all connected collector boards for new measurement results.
  \item Forward measurement results over Ethernet.
  \item Provide a user interface for easy configuration and debugging.
\end{itemize}
We implemented these requirements in two abstract tasks: one for acquiring measurements and sending them
over Ethernet and an other one for handling the user interface.
\subsubsection{Running tasks in parallel}
As these tasks mentioned above should run in parallel, we implemented a modified event loop approach. We
implemented a function for each task, which allow us to execute the abstract tasks
in a semi parallel way:\\
In the main program loop, the two functions are called in turn. Each function however has to guarantee to
not block program execution for more time than is absolutely necessary. Especially waiting for I/O
should not be done via busy waiting. Respecting this constraint, one function
call is most of the time not sufficient to finish a task, but only does some progress on the
current task. For example receiving of a measurement result needs multiple calls
of the corresponding receive function. This is implemented using state machines and different
return values for `task finished' or `task needs more time'.\\
However both the user interface task, as well as the measurement task may access shared resources
like the I2C bus. As semi parallel access will lead to undefined behavior, shared resources
have an associated mutex, which has to be acquired before accessing the resource.\\
\textbf{Note} that implementing
busy waiting when trying to acquire a mutex will immediately lead to a deadlock, due to the nature
of the event loop approach.
\subsubsection{Receiving of measurement results}
The task for acquiring measurements is done in the following steps:
\begin{enumerate}
  \item In the main event loop the function \texttt{loop\_sample()} is called periodically. To trigger the sampling process in fixed time
    intervals, an interrupt generating timer is used to count the time in millisecond resolution. This is already implemented in the Arduino core library
    and initialized using the \texttt{init()} function at startup.
    On each call of the \texttt{loop\_sample()} function in IDLE state, it is determined according to the current millisecond time,
    whether sampling should be started.
  \item As soon as sampling should be started, the mutex for the TWI bus will be acquired. Then a TWI bus scan will be performed, to detect
    all connected collector boards. The result of this scan is required later, when reading the measurement results from each board.
  \item After that, the \texttt{twi\_start\_measurement()} function is called, to send a measurement request to the broadcast address $0x00$.
    This triggers all connected collector
    boards to simultaneously sample all 8 connected sensors.
  \item Now the Ethernet board tries to receive data from each collector board in turn, by issuing a read request. However, the collector boards
    need some time to finish sampling of all sensors and will hence do I2C clock extension. This is detected by the Ethernet board
    sampling function and the function will return and continue to try receiving data in the next event loop cycle.
  \item Once data from one collector board is received completely, a checksum check is performed on all 8 packets and the corresponding error flag of these packets will be set, if the check failed. Then the data is
    handed over to the networking layer, for distribution over Ethernet.
  \item When all collector boards have been processed, the mutex for the TWI bus is released again.
\end{enumerate}
\subsubsection{TCP/IP networking}
% W5100 driver extension, to support clear receive buffer
In order to implement the data sending task and user interface over Ethernet, we built our TCP/IP networking code on top of the W5100 driver, provided by Arduino. We did not use the \texttt{EthernetServer} interface, as
this did not provide enough flexibility for handling independent TCP connections. Our code works directly with sockets, provided by
the Arduino library \texttt{socket.h}. We also had to extend the W5100 driver, to allow fast clearing of the socket receive buffer,
without reading all received data for performance reasons (\texttt{net\_clear\_rcv\_buf(SOCKET)}).\\
To allow convenient reading and writing to sockets, using the C standard input output library (cstdio), we created an interface
above the sockets, which provides a \texttt{FILE} object, representing a stream. However due to lack of memory, we only created one
stream for all sockets. So multiplexing has to be done when writing/reading to/from different sockets, by telling the stream to switch
to a different socket (\texttt{stream\_set\_socket(sock)}). As the stream utilizes buffers, a stream flush (\texttt{sock\_stream\_flush()})
can be performed to force sending of the buffer contents over the network.\\
The final networking layer provides two essential services:
\begin{enumerate}
  \item A handling function \texttt{net\_dataAvailable(...)}, which is used to process measurement data from collector boards:\\
    This function is called by the measurement sampling task, as soon as data was received from one collector board.
    \begin{itemize}
    \item If sending data to the database is enabled,
    the measured data will be packed into a HTTP packet and then sent to the database
    server, via a reserved TCP client socket.
    As in the experiment a couchDB system\footnote{\url{http://couchdb.apache.org/}} is used as database server,
    which accepts data in JSON format, we use the JSON template showed in figure \ref{lst:json} for organising the whole measured data from the collector board. 
\lstset{style=mathstyle}
\begin{lstlisting}[language=c,xleftmargin=70pt, xrightmargin=70pt,framexleftmargin=10pt,framextopmargin=10pt, framexbottommargin=10pt, caption={JSON template for sending data to the couchDB data base},label={lst:json}]
{
    "type":"data",
    "value":{
                "b%03ds%01dTEM":%03d.%02d,
                "b%03ds%01dHUM":%03d.%02d
            }
}
\end{lstlisting}
    \item If data is requested via user interfaces, the whole measured data will be sent to the corresponding clients in plain text over their associated sockets.
\end{itemize}
  \item An event loop function \texttt{net\_loop()}, which is responsible for the user interface (\texttt{serve()}) and incoming data from the database (\texttt{handle\_db\_response()}):
      \begin{itemize}
          \item \texttt{serve()} implements a TCP server, which is able to handle multiple simultaneous terminal user interface sessions.
A parser will parse incoming data from TCP connections and call matching command handler functions, if the data is recognized as a valid command.
All implemented commands will be introduced in section \ref{sec:uicmd}.
New commands with respective callback functions can be registered in a command array \texttt{struct cmd cmds[]}. \textbf{Note} that, after adding a command, the command counter preprocessor variable \texttt{DEFINED\_CMD\_COUNT} has to be incremented.\\
    \textbf{Care has to be taken}, when accessing shared resources like the I2C bus in a handler, as busy waiting for acquiring the mutex will lead to a deadlock.
        \item \texttt{handle\_db\_response()} handles the received database responses after transmission of each data packet. This is required, in order for the w5100 receive buffer not to overflow.
            If a client enables showing data base responses, incoming responses will be redirected to the user interface,
otherwise the receive queue will be emptied in each loop cycle using \texttt{net\_clear\_rcv\_buf(SOCKET)}.
    \end{itemize}
\end{enumerate}
\subsubsection{String handling}
In C, strings are represented as char arrays. If such arrays are initialized in C code, the data is placed
into the \texttt{.bss} or \texttt{.data} section of the compiled program. During program execution, the whole data
will then be initialized inside the AVR RAM. As our application uses a huge amount of string constants for the user interface and
generation of JSON documents, this approach would use up way more memory in RAM, than we have available on the Atmega328 (2Kbyte).\\
Because of that we use the \texttt{PROGMEM} compiler attribute, which causes the string data to be linked to the \texttt{.text} section.
To access data from text section however, it has to be read directly from flash memory, hence standard string manipulating methods
can not be used. However the avr \texttt{cstdio} library provides alternative methods for string processing (e.g. \texttt{fputs\_P()}
as a replacement for \texttt{fputs()}). Using these, strings are usually read char by char directly from flash memory and a minimum
amount of RAM is used.
\subsubsection{Configuration}
To store the system configuration, we use the Atmega328 integrated EEPROM storage. We also implemented EEPROM wear leveling, to allow
maximum lifetime, even for many configuration changes.\\
\textbf{Note} that for reliable EEPROM persistency, the integrated burnout detection should be enabled, to keep the AVR controller in reset state at voltages below 4.5 V, as the EEPROM shows undefined behavior, if the controller is running at voltages below 4.5 V.
\subsection{User interface commands}
\label{sec:uicmd}
The terminal user interface, which is provided by the Ethernet board over TCP/IP, can be accessed via applications like telnet or netcat.
This allows users to conveniently change or view system settings. The interface is command driven, every command should be terminated
by a newline and/or carrier return character.\\
By default, the user interface is reachable at port 8888.
It is possible to open up to three simultaneous connections to the user interface.\\
Most commands to change the configuration can also be executed, without providing
arguments. The command will then return the current configuration value.\\
The following commands are supported:
\subsubsection{System configuration}
\begin{description}
  \item[help]\hspace{1cm}\\
    All supported commands, needed arguments and their usage will be listed.
  \item[res]\hspace{1cm}\\
    This command stores configuration changes to EEPROM, terminates all current connections and restarts all network
    services.
  \item[sto]\hspace{1cm}\\
    All configuration changes will be stored to EEPROM and hence will be available
    after a system reset.
  \item[c]\hspace{1cm}\\
    This will close the terminal user interface session.
\end{description}
\subsubsection{Network configuration}
\begin{description}
  \item[ip] [ip1.ip2.ip3.ip4/subnet]\\
    The internet address and subnet will be set to the supplied
    values.\\
    Example: ip 10.0.1.42/24
  \item[p] [port]\\
    The TCP port, under which the user interface is reachable will be
    set to the given value.\\
    Example: p 23
  \item[mac] [mac1:mac2:mac3:mac4:mac5:mac6]\\
    The Ethernet MAC address of the device will be set to the given value.\\
    Example: mac 60:76:d3:c4:7a:70
  \item[gw] [gw1.gw2.gw3.gw4]\\
    The internet gateway address is set to the given value.\\
    Example: gw 10.0.1.1
\end{description}
    \textbf{Note}, that changes to network settings only get effective, after the \emph{res} command is executed, or after storing the new settings first using the \emph{sto} command and then resetting the system.
\subsubsection{Database configuration}
\begin{description}
  \item[d.s] [ 1 $|$ 0 ]\\
    Enables or disables the sending of measurement results to the database. If the
    argument is \emph{1}, sensor values will be sent to the database, if the argument
    is \emph{0} nothing will be transmitted to the database.\\
    Example: d.s 1
  \item[d.ip] [ip1.ip2.ip3.ip4]\\
    Sets the IP address, under which the couchDB database is reachable.\\
    Example: d.ip 10.0.1.9
  \item[d.p] [port]\\
    Sets the TCP port, under which the couchDB database HTTP interface is reachable.\\
    Example: d.p 5984
  \item[d.ck] [cookie]\\
    Configures the cookie, used for authentication with the couchDB database.\\
    \textbf{Note} that the length of the argument is limited. To get the maximum allowed
    length for this command, use the \emph{help} command.\\
    Example: d.ck YXJkdWlub190ZW1wZXJhdHVyZV93cml0ZXI6
  \item[d.n] [db\_name]\\
    Configures the couchDB database name, to which sensor values will be stored.\\
    \textbf{Note} that the length of the argument is limited. To get the maximum allowed
    length for this command, use the \emph{help} command.\\
    Example: d.n nedm/temperature\_environment
  \item[d.d] [document\_name]\\
    Specifies the name of the JSON document, to write the measurement values to.\\
    \textbf{Note} that the length of the argument is limited. To get the maximum allowed
    length for this command, use the \emph{help} command.\\
    Example: d.d nedm\_default
  \item[d.f] [filename]\\
    Specifies the name of the function used, to insert data into the database.\\
    \textbf{Note} that the length of the argument is limited. To get the maximum allowed
    length for this command, use the \emph{help} command.\\
    Example: d.f insert\_with\_timestamp
  \item[d.v]\hspace{1cm}\\
    This toggles forwarding of the database HTTP response to the current terminal.
    This is useful for debugging database configuration problems.\\
    \textbf{Note} that forwarding has a huge impact on the system performance and should be
    disabled during normal operation.
  \item[d.re]\hspace{1cm}\\
    This command stores configuration changes to EEPROM and resets all network
    connections to the database.
\end{description}
\subsubsection{Sensor network configuration}
\begin{description}
  \item[s] \hspace{1cm}\\
    This causes a I2C bus scan to be performed. Scanning addresses in the range from
    8 to 120. After the scan, a list of connected I2C devices will be printed out.
  \item[v] \hspace{1cm}\\
    This toggles forwarding of measurement results to the current terminal.\\
    \textbf{Note} that forwarding has a huge impact on the system performance and should be
    disabled during normal operation.
  \item[i] [interval]\\
    Configures the sampling interval in seconds. No floating point values are allowed.
    A value of 0 causes the system to sample at maximum rate, which is typically
    between 1 Hz and 2 Hz, depending on the amount of connected collector boards.\\
    Example: i 5
  \item[ba] old\_address new\_address\\
    Changes the address of a connected collector board.\\
    Example: ba 13 22
  \item[led] board\_addr led\_number (1 $|$ 0)\\
    Controls the LEDs of connected collector boards. The LED with the corresponding number
    will be turned on (1) or off (0). It is currently not possible, to read the state of the LEDs.\\
    Example: led 13 2 1
\end{description}
%###############################################################
\chapter{Deployment}
%%%%%%%%%%%%%%%%%%%%%%%%%%%%%%%%%%%%%%%%%%%%%%%%%%%%%%%%%%%%%%%
\section{Casings for the hardware}
Casings for the electronic components were designed with 3D CAD software and then printed with the department's 3D printer. The 3D
files of each case can be found in our GIT repository. Figure \ref{fig:casings} shows the completed cases with circuit boards inside.
\begin{figure}[Hh!]
	\centering
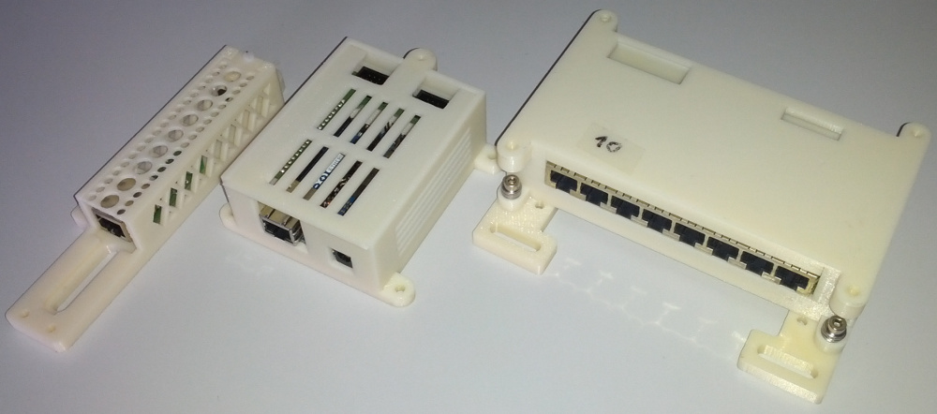
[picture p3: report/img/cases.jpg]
	
  \caption{3D printed casings. Left: temperature board casing, middle: Ethernet board casing, right: collector board casing. The casing for the humidity board is not shown, as it is similar to the one for the temperature sensor, but longer.}
	\label{fig:casings}
\end{figure}
\paragraph{Casings for the sensors}\hspace{1cm}\\
The casings for the sensor boards were designed to protect the sensors from being damaged, as well as to provide a convenient way of
mounting them on ITEM compatible aluminium profiles. The casing walls have a mesh structure, to allow maximum air exchange around the
sensor. To prevent damage of the sensor board, caused by the Ethernet cable, a strain-relief is also featured. The original design and
idea for the sensor casings was done by Tobias Lins.
\paragraph{Casings for the control units}\hspace{1cm}\\
We also designed cases for the Ethernet and collector boards, to be able to mount them in an easy and compact manner.\\
Cases for the collector board were designed to be stackable. This works well with the I2C chaining feature, as to extend the sensor network,
only a new collector board has to be placed on top of the stack. The I2C plug can then be connected to the socket of the topmost board, and provides
communication and power to the new board.
%%%%%%%%%%%%%%%%%%%%%%%%%%%%%%%%%%%%%%%%%%%%%%%%%%%%%%%%%%%%%%%
\section{Installation}
\paragraph{Sensor distribution}\hspace{1cm}\\
In total we installed 42 temperature sensors and 2 humidity sensors inside the field
cage of the nEDM experiment setup. For convenient cable routing, we used
two control stations, each consisting out of three stacked collector boards and one
Ethernet board. One of the control stations is placed on the ceiling of the
topmost floor and the other one is placed near the ground in the lowest floor. We tried
to distribute the sensors evenly in the field cage. However, most
of the sensors were placed on the walls and ceilings of the individual floors. 
Figure
\ref{fig:install} shows the approximate distribution of sensors and control stations.\\
The two control stations feature sockets for 48 sensors, as we currently only use 44,
the remaining four sockets can be used, to connect additional sensors on demand\footnote{\textbf{Note}, that
the system is Plug and Play. This means the sensors may be connected and disconnected
while the system is running.}.
\paragraph{Cable routing}\hspace{1cm}\\
As cables to connect the sensors we used shielded CAT.5e cables, with lengths between 3 and 15 meters.
We attached two unique identifier tags to each cable, connecting a sensor to a collector
board. This ID specifies, to which collector board and to which exact socket,
the cable should be connected. For example, the ID 'B013S0' means, that the cable should
be connected to collector board number 13 in the leftmost socket. The board number by default is identical to the I2C address of the collector board.\\
The cables leading to sensors, were collected in cable channels where possible and otherwise
fastened with cable straps to the cage skeleton.\\
Figure \ref{fig:control_unit} shows an installed control station with connected cables to
the individual sensors. In this case the power supply is a 9V switching power supply, connected
to one of the collector boards. The integrated Voltage regulator of this board then creates
a 5V output, which drives all three collector boards via the I2C connection.
%%%%%%%%%%%%%%%%%%%%%%%%%%%%%%%%%%%%%%%%%%%%%%%%%%%%%%%%%%%%%%%
\section{Problems}
\subsection{Squid magnetic field measurement}
To detect possible magnetic interference of our sensor network with the nEDM experiment,
we performed two measurements, where
we placed 10 sensors and 6 collector boards inside the magnetically shielded room and performed
magnetic field measurements using a squid magnetometer. However both our measurements were
influenced by time dependant noise, which made the results not trustworthy.
\subsection{Crash after long uptime}
\paragraph{The problem}\hspace{1cm}\\
The software on the Ethernet board currently contains a bug, which causes the board to
crash at semi-random times. As a result the Ethernet board becomes completely inoperable.
The occurrence of this problem is dependent on the configured sampling rate. At a sampling
interval of $5\,s$ it occurs after about 8 hours, at $\approx0.6\,s$ it occurs already after about
2 hours. Due to the random nature however, these time values represent mean values based on
observations.\\
After debugging, we found out, that the program is always crashing in the function
\texttt{net\_sendResultToDB(struct dummy\_packet *packets, uint8\_t board\_addr)}. We also found out, that the first part of the function executes correctly:
\definecolor{mygreen}{rgb}{0,0.6,0}
\lstdefinestyle{customc}{
  belowcaptionskip=1\baselineskip,
  breaklines=true,
  %frame=L,
  %xleftmargin=\parindent,
  language=C,
  showstringspaces=false,
  basicstyle=\footnotesize\ttfamily,
  %keywordstyle=\bfseries\color{green!40!black},
  %commentstyle=\itshape\color{purple!40!black},
  keywordstyle=\bfseries\color{mygreen},
  commentstyle=\itshape\color{blue},
  identifierstyle=\color{black},
  stringstyle=\color{red}
}
\lstset{style=customc}
\begin{lstlisting}[language=C, framextopmargin=10pt, framexbottommargin=10pt]
void net_sendResultToDB(struct dummy_packet *packets, uint8_t board_addr){
  // Sends a set of 8 measurement results to the couchdb database
  int8_t sensor_index;
  int8_t comma_flag = 0;
  int16_t value;
  uint16_t len=0;
  PORTB &= ~(1<<PB1);
  PORTD &= ~(1<<PD5);
  if( W5100.readSnSR(DB_CLIENT_SOCK) != SnSR::ESTABLISHED ){
    if(!connect_db(cfg.port+1)){
      return;
    }
  }
  // CRASH OCCURS SOMEWHERE AFTER THIS LINE:
  // Calculate length for the JSON header:
  for (sensor_index=0; sensor_index<8; sensor_index++){
    if(packets[sensor_index].header.error && packets[sensor_index].header.connected){
      // We do not send data, which might have an error
      continue;
    }
    if(packets[sensor_index].header.connected){
      switch(packets[sensor_index].header.type){
        case PACKET_TYPE_TSIC:
...
...
\end{lstlisting}
However we did not have enough time to exactly locate the problematic code.
\paragraph{The workaround}\hspace{1cm}\\
We implemented a workaround for this problem, using the integrated watchdog
timer (WDT) of the atmega88. This is a independent timer of the
controller, which can be reset via software. If a overflow of this timer occurs,
a complete system reset of the chip will be performed. In our configuration, we
trigger a timer reset of the WDT on specific points during program execution.
If however the mentioned bug occurs, the program will hang and after a timeout
a system reset will occur. 
This approach may also handle further bugs, which cause the system to hang.
On one hand, it makes the system more robust by allowing it to receiver by itself,
but on another hand, this will make hidden problems difficult to find. 
Therefore, it can only be seen as a temporary solution, especially as after a crash,
timing of the measurement interval will not be right
for one measurement, as a crash might cause a blackout for up to 15 seconds.
\paragraph{Further debugging ideas}\hspace{1cm}\\
While debugging, we found out, that printing debug information over the USART
interface will heavily extend the time until the bug appears, so this is not a
good option for debugging the code. We had most success, to locate the bug,
by changing the state of LEDs or other GPIOs at different code locations. After
the system has crashed, we could just look at the LEDs or measured the voltage on
GPIO pins to see which line was still executed.
\subsection{Minor problems}
\subsubsection{Range of I2C}
In the design phase, we decided to use I2C for communication between
the collector boards. This decision was made, because I2C features clock
extension and is flexible with regards to connecting new bus participants.\\
The drawback of this protocol however is, that it is not suitable for long
range communication, due to the pullup resistors, which allow dominant
bits. It would be possible to transfer I2C signals over a CAN physical layer
network, to increase range, however we did not implement this, due to
cost and complexity savings.\\
During deployment, we realized, that this is a weak point of our sensor
network, as we were limited to star shaped network topologies. In the case
for the nEDM experiment, this problem was not severe, as we only needed
two control points to conveniently route cables to all sensors from there.
So we used two ethernet boards, which was still more efficient in terms
of total cost, than using a CAN network.\\
However for bigger networks this would represent a drawback.
\subsubsection{Plug and Play with I2C}
Due to the many different bus states and undefined behavior, when bus
participants are connected / disconnected during bus transactions, it was
very difficult to allow plug and play of collector boards on the I2C bus.\\
The current implementation works very stable, however we can not guarantee
safe operation, when the device configuration changes during runtime, even though
we did not observe a crash in our tests.\\
This problem does not affect normal operation, as in the current setup in the
nEDM experiment, no collector boards will be added or removed during runtime.
If collector boards are changed and then the network freezes, a power cycle for the collector boards might have to be performed or a restart the system.
\\
However, Plug and Play for the individual sensors works perfectly.
\subsubsection{Low fault tolerance of I2C}
Due to the nature of the bus, one failing I2C bus participant might be able to
block the whole bus, rendering the whole network unusable.
\textbf{Note} that this
might happen, when the micro controller is connected to a USBasp programmer,
which is not connected to a computer.
%%%%%%%%%%%%%%%%%%%%%%%%%%%%%%%%%%%%%%%%%%%%%%%%%%%%%%%%%%%%%%%
\section{Developing / Extending}
\subsection{Project git repository}
Our whole project can be found at GitHub under nEDM-TUM. The repository name is ``Temperature-Sensor-System''. The repository URL is \url{https://github.com/nEDM-TUM/Temperature-Sensor-System}. Figure \ref{lst:git} show the directory structure of the repository.
\lstset{style=mathstyle}
\begin{lstlisting}[language=c,xleftmargin=25pt, xrightmargin=25pt,framexleftmargin=10pt,framextopmargin=10pt, framexbottommargin=10pt, caption={Directory structure in the project git repository}, label={lst:git}]
.
+-- casings     // 3D CAD files for 3D printer
|   +-- adapter
|   +-- arduino
|   +-- cable_clamp
|   +-- collector
|   +-- humidity
|   +-- temperature
+-- circuit_boards      // Circuit schematic diagram and 
|   |                   // PCB schematic files created using KiCad
|   +-- 3x127_254_adapter       // A PCB chip adapter, 
|   |                           // used for breadboard debugging
|   +-- 4x127_254_adapter       // A PCB chip adapter, 
|   |                           // used for breadboard debugging
|   +-- arduino_adapter
|   +-- humidity
|   +-- kicad_library           // Footprint and Component
|   |                           // library files for KiCad
|   +-- order           // PCB assembly, which was sent to 
|   |                   // Fischer Leiterplatten for production
|   +-- sensor_board
|   +-- so8_breakout    // A PCB chip adapter, 
|   |                   // used for breadboard debugging
|   +-- temperature_board
+-- datasheets      // Datasheets for sensors, micro processor, etc.
+-- presentation    // Slides (tex files) for a project presentation
+-- registration    
|   +-- description     // Project description (tex files) 
|                       // used for registration
+-- report      // Main project documentation (tex files)
+-- shop_orders // Receipts of orders from hardware shops
+-- sofware
|   +-- avr_wcet_analyzer   // code of a WCET analyzer
|   |                       // for the AVR instruction set
|   +-- collector_board      
|   +-- ethernet_board        
|   +-- humidity_board      
|   +-- util        // Commonly used utility code
+-- squid_analysis      
|   +-- data            // Squid magnetic field measurement protocol.
|                       // For squid data please write a mail to us.
|   +-- evaluation      // Evaluation script of squid analysis data
\end{lstlisting}
\subsection{Tips}
The following are tips for developers, which might be useful, when extending
the sensor network:
\begin{itemize}
\item To prevent EEPROM from being corrupted on power cycles, the AVR
  integrated brownout detection should be enabled.
\item To allow EEPROM storage to stay intact after reprogramming, set the
  corresponding fuse bit.
\item As Arduino fuses are not possible to be programmed via the default Arduino
  programmer (using the Arduino boot loader), we removed the boot loader and use
  the ISP connector for programming (see section \ref{chap:isp}).
\item To not overload the voltage regulator, especially when driving multiple
  boards one should consider, that a significant portion of power is used to
  drive LEDs ($\approx20\,\mathrm{mA}$ per LED). So turning the LEDs off during
  normal operation will prevent overheating.
\item When debugging and programming devices of the sensor network, one has to
  be very careful, to not provide different power sources, as this might cause
  unexpected results, which can lead to damage of the sensor network, as well
  as connected computers. By default the USBasp programmer provides the system
  with 5V power.
\item Our makefiles currently do not support automatic detection of
  file dependencies, and source files to be compiled. All source files have to
  be specified explicitly and if changes to header files are made, a 'make clean'
  should be performed before compiling the program.
\item Be careful, when using the USART line or similar for generating debugging
  output. Transmitting debugging information takes relatively long time and might
  influence the system heavily, especially, when debugging timing critical code.
  LEDs or GPIO pins with an oscilloscope provide a faster but more complex way for debugging.
\end{itemize}
%###############################################################
\chapter{References}
%\renewcommand\refname{\vskip -1cm}
%\bibliographystyle{abbrv}
\bibliographystyle{plain}
\begingroup
\def%###############################################################
\chapter*#1{}
\bibliography{bib}
\endgroup
%\bibliography{bib}
\nocite{*}

\begin{appendices}
%###############################################################
\chapter{Board Schematics}
\begin{figure}[Hh!]
	\centering
	
	\caption{Temperature board schematic. The Impedance adjuster circuit, R4 and C4 is not required to be populated, as we only transmit data.}
	\label{fig:schem_temp}
\end{figure}
\begin{figure}[Hh!]
	\centering
	
	\caption{Humidity board schematic.The Impedance adjuster circuit, R6 and C5 is not required to be populated, as we only transmit data.}
	\label{fig:schem_hum}
\end{figure}
\begin{figure}
	\centering
	
	\caption{Collector board schematic}
	\label{fig:schem_collect}
\end{figure}
%###############################################################
\chapter{Board PCB layout}
\begin{figure}[Hh!]
	\centering
	
	\caption{Temperature printed circuit board schematic. Ground planes are not displayed.}
	\label{fig:pcb_temp}
\end{figure}
\begin{figure}[Hh!]
	\centering
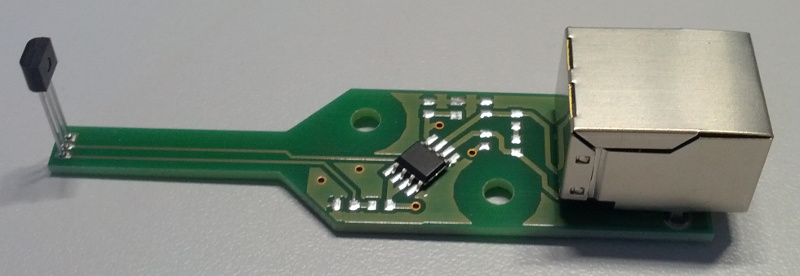
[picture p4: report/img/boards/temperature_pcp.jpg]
	
	\caption{Temperature printed circuit board. Components not completely soldered yet.}
	\label{fig:soldered_temp}
\end{figure}
\begin{figure}[Hh!]
	\centering
	
	\caption{Humidity printed circuit board schematic. Ground planes are not displayed.}
	\label{fig:pcb_hum}
\end{figure}
\begin{figure}[Hh!]
	\centering
	
	\caption{Collector board printed circuit board schematic. Ground planes are not displayed.}
	\label{fig:pcb_collector} 
\end{figure}
\begin{figure}[Hh!]
	\centering
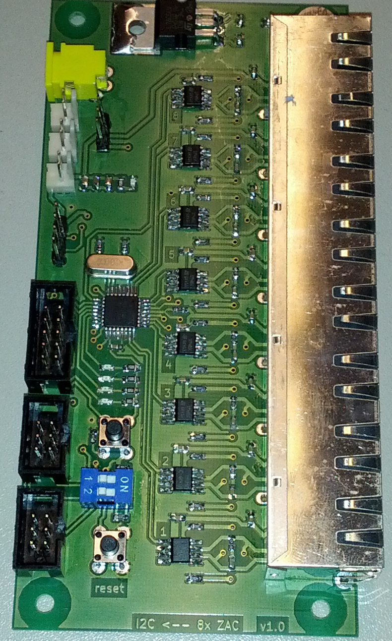
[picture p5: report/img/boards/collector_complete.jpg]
	
	\caption{Collector printed circuit board, completely soldered.}
	\label{fig:soldered_col}
\end{figure}
\begin{figure}[Hh!]
	\centering
	
	\caption{Arduino adapter printed circuit board schematic. Ground planes are not displayed.}
	\label{fig:pcb_arduino} 
\end{figure}

%###############################################################
\chapter{Installation images and schematics}
\begin{figure}[Hh!]
	\centering
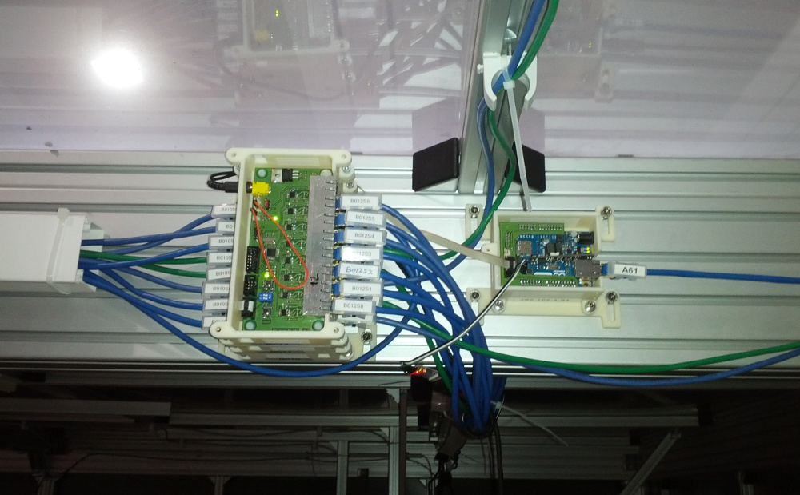
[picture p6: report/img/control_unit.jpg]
	
	\caption{One of the two installed control units, consisting of three stacked collector boards and one Ethernet board. The lids of the casings are removed here. Every cable to a sensor is marked with an unique identifier.}
	\label{fig:control_unit} 
\end{figure}
\begin{figure}[Hh!]
	\centering
	
  \caption{Approximate sensor distribution in the field cage.}
	\label{fig:install}
\end{figure}
\end{appendices}

\end{document}

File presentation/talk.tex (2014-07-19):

\documentclass[t]{beamer}
\usepackage{helvet}
\usepackage{calc}
\usepackage[utf8]{inputenc} % set your input encoding differently, if you want
\usepackage[english]{babel}

% Setting style of presentation
% =============================
\usetheme{Boadilla}
%\setbeamercovered{transparent=10}
%\setbeamertemplate{navigation symbols}{}

% Some common packages
% ====================
\usepackage{units}
\usepackage{amsbsy}
\usepackage{amsmath}
\usepackage{amssymb}
\usepackage{graphics}
\usepackage{epsf}
\usepackage{epsfig}
\usepackage{fixmath}
\usepackage{wrapfig}
\usepackage{tcolorbox}

\usepackage{bytefield}

\usepackage{array}
\newcolumntype{M}{>{\centering\arraybackslash}m{\dimexpr.25\linewidth-2\tabcolsep}}

% Adapt title information
% =======================
\title{Development of a temperature sensor network\\for the nEDM experiment}
\author{Wenwen Chen, Rainer Schönberger}
%\institute{Department for Computer Science\\Technische Universität München}
\date{\today}

% ==============
% DOCUMENT BEGIN
% ==============
\begin{document}

% Typeset title page
% ------------------------------------------------------------------------
%\setbeamertemplate{background}{\NETBlackTransparent{width=2.3\paperwidth}}
\begin{frame}
    \titlepage
\end{frame}
%\setbeamertemplate{background}{}
% ------------------------------------------------------------------------

% Outline
% ------------------------------------------------------------------------
%\begin{frame}
%    \frametitle{Outline}
%    \tableofcontents
%\end{frame}
% ------------------------------------------------------------------------

% MOTIVATION
% ------------------------------------------------------------------------
\begin{frame}[c]
    \frametitle{Requirements}
		\begin{alertblock}{Must}
			\begin{itemize}
				\item Temperature and humidity measurement
				\item High accuracy: $\pm0.1\mathrm{K}$
				\item High number of sensors: $\approx$ 40
        \item Low cost
				\item Send results to couchDB
        \item Ready to use 
				\item Reliable and stable
			\end{itemize}
		\end{alertblock}
\end{frame}
\begin{frame}[c]
    \frametitle{Requirements}
		\begin{exampleblock}{May}
			\begin{itemize}
				\item Extendible
        \item Easy maintenance
				\item Plug and Play
				\item Sample interval $\le 1\mathrm{s}$
				\item Easy configuration at runtime
			\end{itemize}
		\end{exampleblock}
\end{frame}
\begin{frame}[c]
    \frametitle{Components structure}
  \begin{center}
  	\\
  \vspace{0.5cm}
  \end{center}
\end{frame}
\begin{frame}[c]
    \frametitle{Hardware}
\begin{tabular}{ M M M M}
	Sensor & Accuracy & Resolution & Cost\tabularnewline
	\hline
	\hline
	TSIC 506F& $\pm 0.1\mathrm{K}$ & $\pm 0.034\mathrm{K}$ & $8 \mathrm{EUR}$\tabularnewline
	\hline
	HYT271 & $\pm 1.8\mathrm{\%RH}$ & $\pm 0.03\mathrm{\%RH}$ & $20 \mathrm{EUR}$\tabularnewline
	& $\pm 0.2\mathrm{K}$ & $\pm 0.015\mathrm{K}$ & \tabularnewline
	\hline
\end{tabular}
\end{frame}
\begin{frame}[c]
    \frametitle{Proof of concept}
  \begin{center}
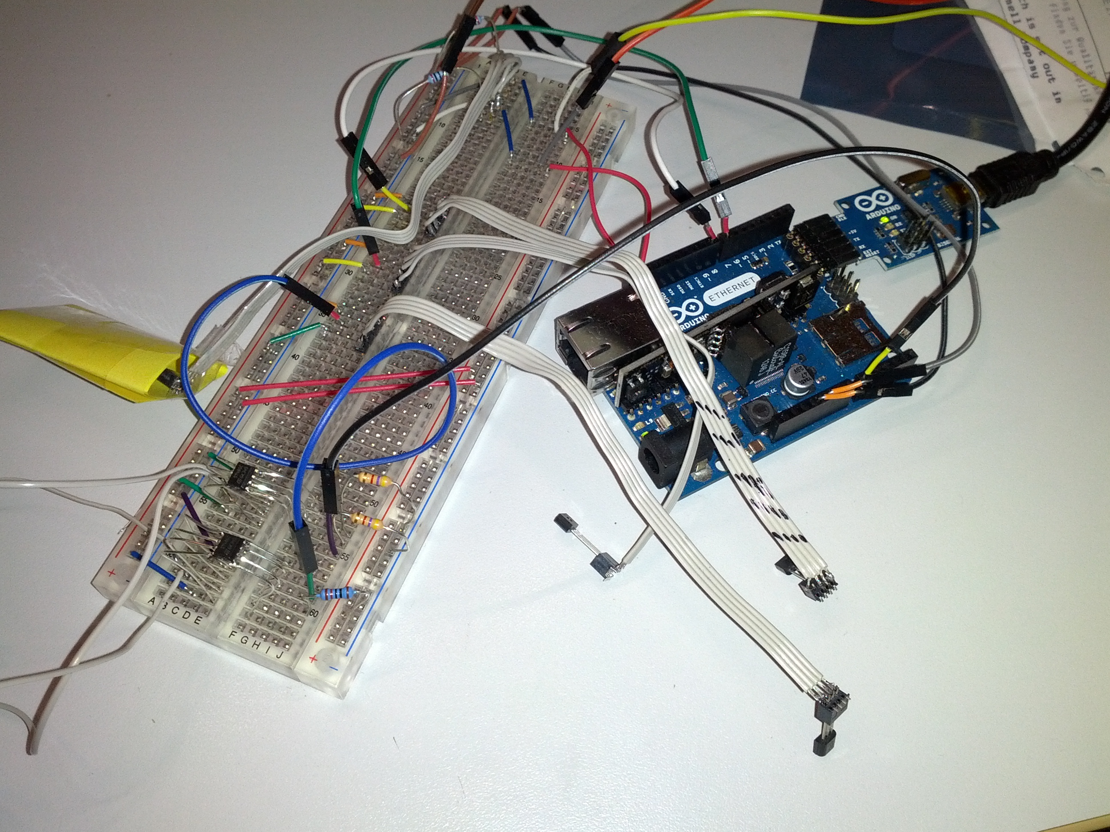
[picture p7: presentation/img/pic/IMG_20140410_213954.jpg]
  	\\
  \vspace{0.5cm}
  \end{center}
\end{frame}
\begin{frame}[c]
    \frametitle{First load of PCBs arrived}
  \begin{center}
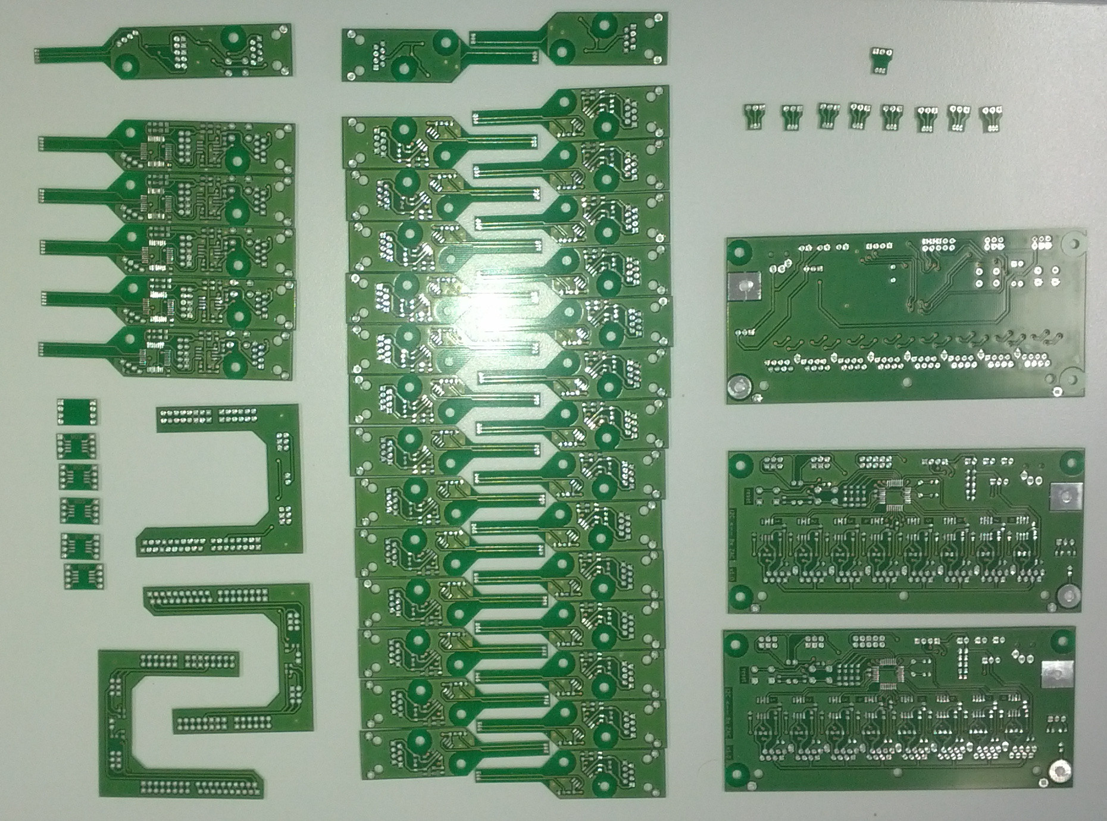
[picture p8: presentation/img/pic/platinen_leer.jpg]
  	\\
  \vspace{0.5cm}
  \end{center}
\end{frame}
\begin{frame}[c]
    \frametitle{Hours of soldering later...}
  \begin{center}
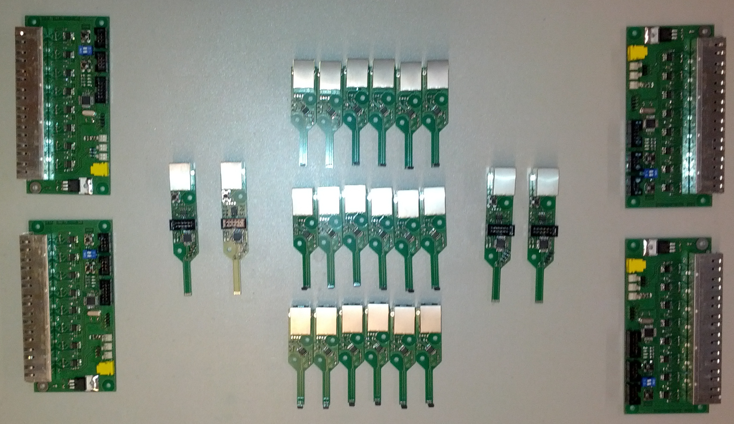
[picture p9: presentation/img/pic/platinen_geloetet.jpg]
  	\\
  \vspace{0.5cm}
  \end{center}
\end{frame}
\begin{frame}[c]
    \frametitle{Collector board}
  \begin{center}
  	\\
  \vspace{0.5cm}
  \end{center}
\end{frame}
\begin{frame}[c]
    \frametitle{Material cost per board}
		\begin{description}
			\item{\textbf{Collector board:}} 20 EUR
			\item{\textbf{Temperature board:}} 12 EUR
			\item{\textbf{Humidity board:}} 30 EUR
		\end{description}
\end{frame}
\begin{frame}[c]
    \frametitle{Components structure}
  \begin{center}
  	\\
  \vspace{0.5cm}
  \end{center}
\end{frame}
\begin{frame}[c]
    \frametitle{ZAC Protocol}
  \begin{center}
  	\\
  \vspace{0.5cm}
  \end{center}
\end{frame}
\begin{frame}[c]
    \frametitle{ZAC Timing}
  \begin{center}
  	\\
  \vspace{0.5cm}
  \end{center}
\end{frame}
\begin{frame}[c,fragile]
    \frametitle{I2C Protocol - Command}
  \begin{center}
	\begin{bytefield}[endianness=big, bitwidth=2em]{8}
		\bitheader{0-7}\\
		\bitbox{7}{Address} &
		\bitbox{1}{R/W}\\
		\wordbox{1}{Command}\\
		\wordbox{1}{Argument}
	\end{bytefield}
  \end{center}
\end{frame}
\begin{frame}[c,fragile]
    \frametitle{I2C Protocol - Receive}
  \begin{center}
		\begin{bytefield}[endianness=big, bitwidth=2.1em]{8}
		\bitheader{0-7}\\
		\begin{rightwordgroup}{Header}
			\bitbox{2}{type} & \bitbox{3}{\color{lightgray}\rule{\width}{\height}} & \bitbox{1}{c} & \bitbox{2}{error}
		\end{rightwordgroup}\\
		\begin{rightwordgroup}{Payload}
			\wordbox{2}{Temperature}\\
			\wordbox{2}{Humidity}
		\end{rightwordgroup}\\
		\wordbox{1}{CRC-8}
	\end{bytefield}
  \end{center}
\end{frame}
\begin{frame}[c]
    \frametitle{couchDB}
  \begin{center}
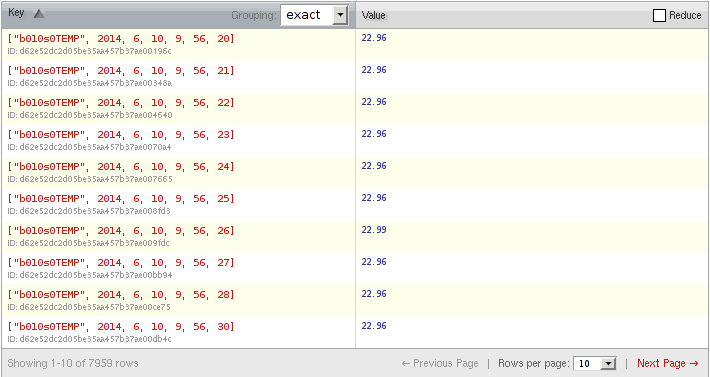
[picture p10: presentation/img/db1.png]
  	\\
  \vspace{0.5cm}
  \end{center}
    
\end{frame}
\begin{frame}[c]
    \frametitle{couchDB}
  \begin{center}
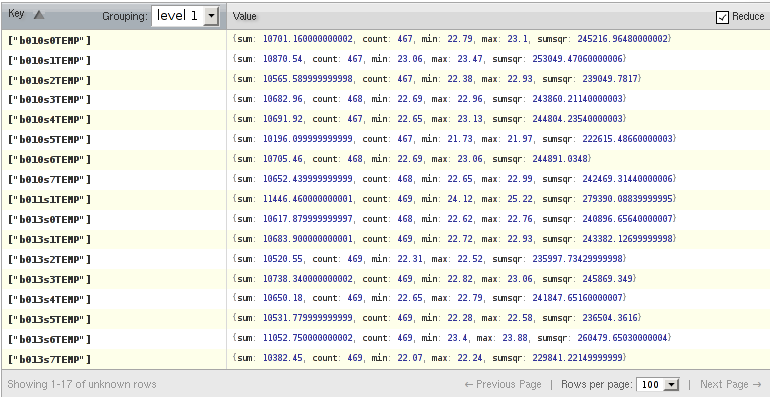
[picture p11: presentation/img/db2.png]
  	\\
  \vspace{0.5cm}
  \end{center}
\end{frame}
\begin{frame}[c]
    \frametitle{User interface}
  \begin{center}
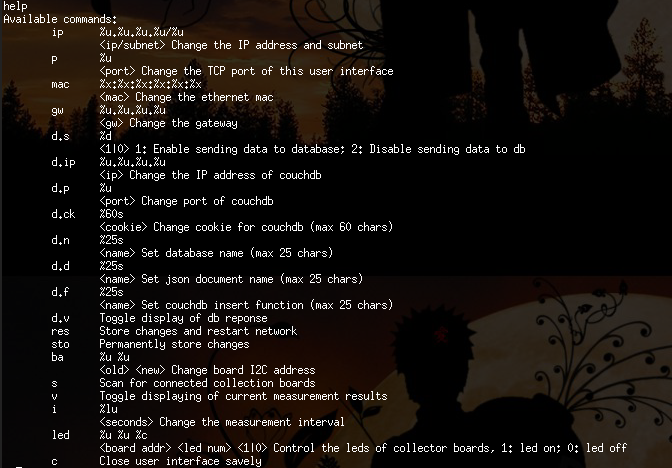
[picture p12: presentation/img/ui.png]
  	\\
  \vspace{0.5cm}
  \end{center}
\end{frame}
\begin{frame}[c]
    \frametitle{User interface}
  \begin{center}
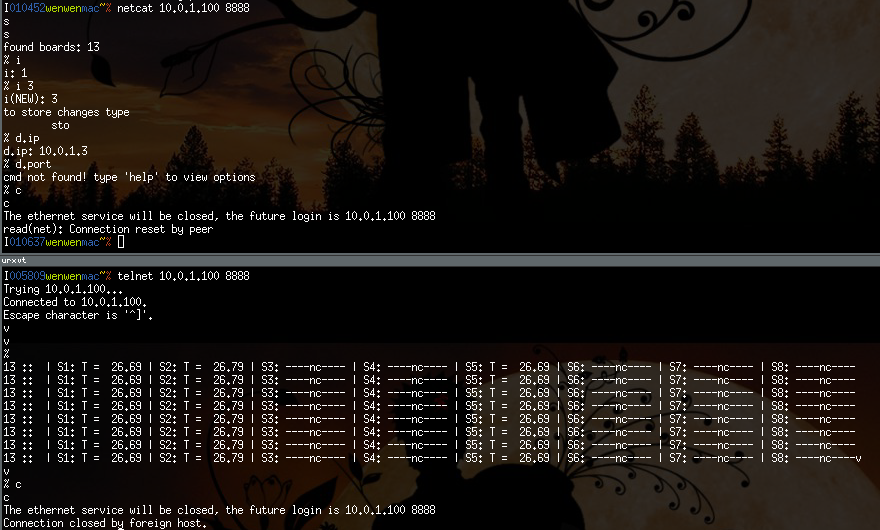
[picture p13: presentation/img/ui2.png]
  	\\
  \vspace{0.5cm}
  \end{center}
\end{frame}
\begin{frame}[c]
    \frametitle{Ready to install}
  \begin{center}
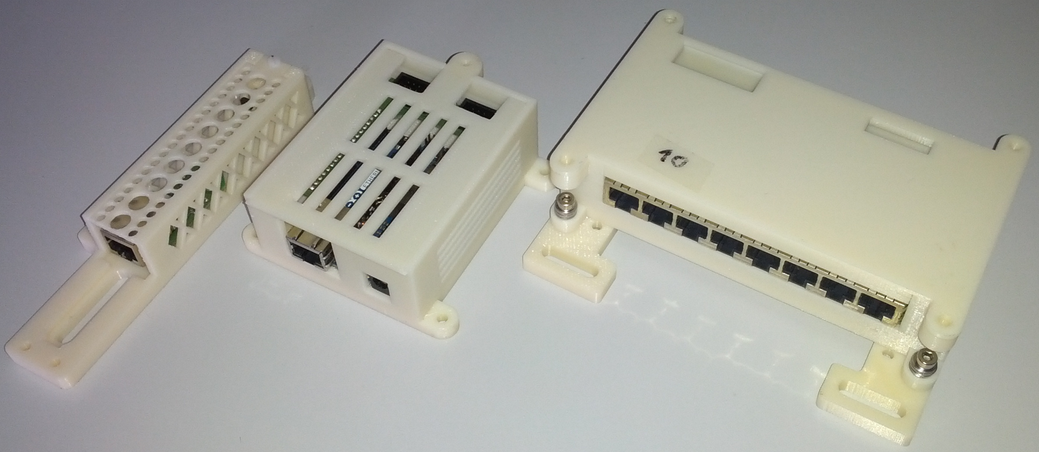
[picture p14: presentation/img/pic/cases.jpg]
  	\\
  \vspace{0.5cm}
  \end{center}
\end{frame}
\begin{frame}[c]
    \frametitle{Ready to install}
  \begin{center}
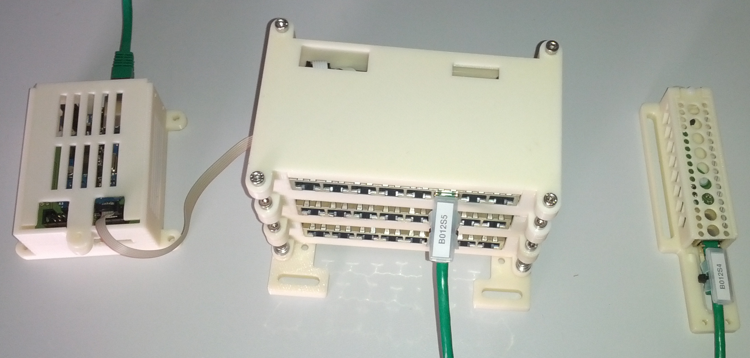
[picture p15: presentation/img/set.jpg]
  	\\
  \vspace{0.5cm}
  \end{center}
\end{frame}
%\begin{frame}[c]
%    \frametitle{3D - Printing}
%  \begin{center}
%  	\includegraphics[width=0.8\linewidth]{img/pic/IMG_20140530_184940.jpg}\\
%  \vspace{0.5cm}
%  \end{center}
%\end{frame}
\begin{frame}[c]
    \frametitle{Distribution in the field cage}
  \begin{center}
  	\\
  \vspace{0.5cm}
  \end{center}
\end{frame}
\begin{frame}[c]
    \frametitle{Improvements}
		\begin{alertblock}{Problems}
			\textcolor{blue!30!green}{
				\begin{itemize}
					\item DHCP
					\item DNS
					\item Cases
				\end{itemize}
			}
		\end{alertblock}
\end{frame}
\end{document}

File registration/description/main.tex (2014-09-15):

% Cover letter using letter.cls
\documentclass[a4paper]{article} % Uses 10pt
%\usepackage{helvetica} % uses helvetica postscript font (download helvetica.sty)
%\usepackage{newcent}   % uses new century schoolbook postscript font 
\usepackage[utf8]{inputenc}       % allow Latin1 characters
\usepackage{graphicx}
% the following commands control the margins:
%\topmargin=-1in    % Make letterhead start about 1 inch from top of page 
%\textheight=8.5in    % text height can be bigger for a longer letter
%\oddsidemargin=0pt   % leftmargin is 1 inch
%\textwidth=6.5in     % textwidth of 6.5in leaves 1 inch for right margin
\title{Implementierung eines Temperatur und Luftfeuchtigkeits Sensornetzwerks für den nEDM Experiment Aufbau\\-\\IDP Kurzbeschreibung}
\author{Wenwen Chen, Rainer Schönberger}
\begin{document}
\maketitle
\section*{Das nEDM Experiment}
\subsection*{Überblick}
Nach dem Standardmodell der Teilchenphysik wird derzeit angenommen, dass
Neutronen durch elektroschwache Wechselwirkung ein elektrisches Dipolmoment
in der Größenordnung von etwa $10^{-32}e\cdot cm$ haben. Eine Erweiterung des
Standardmodells wird ein Dipolmoment des Neutrons bereits im Bereich zwischen
$10^{-26}e\cdot cm$ und $10^{-28}e\cdot cm$ vorhergesagt. Derzeit liegt das
Limit für Messungen des Dipolmoments bei ca. $10^{-26}e\cdot cm$\\
Das Neutron EDM Experiment an der TUM versucht deshalb die Messgenauigkeit so
weit zu steigern, damit die oben genannte Theorie entweder belegt oder
widerlegt werden kann.\\
Um dies zu erreichen, werden spinpolarisierte ultrakalte Neutronen (UCN) in
zwei Kammern in einer hochgradig kontrollierten und magnetisch abgeschirmten
Umgebung (siehe Abbildung \ref{fig:exp}) gefüllt. Dort wird dann eine
Spin\-präzessions\-messung nach Ramsey
durchgeführt, mit welcher Informationen über das elektrische Dipolmoment des
Neutrons gewonnen werden.
\begin{figure}[h]
\centering
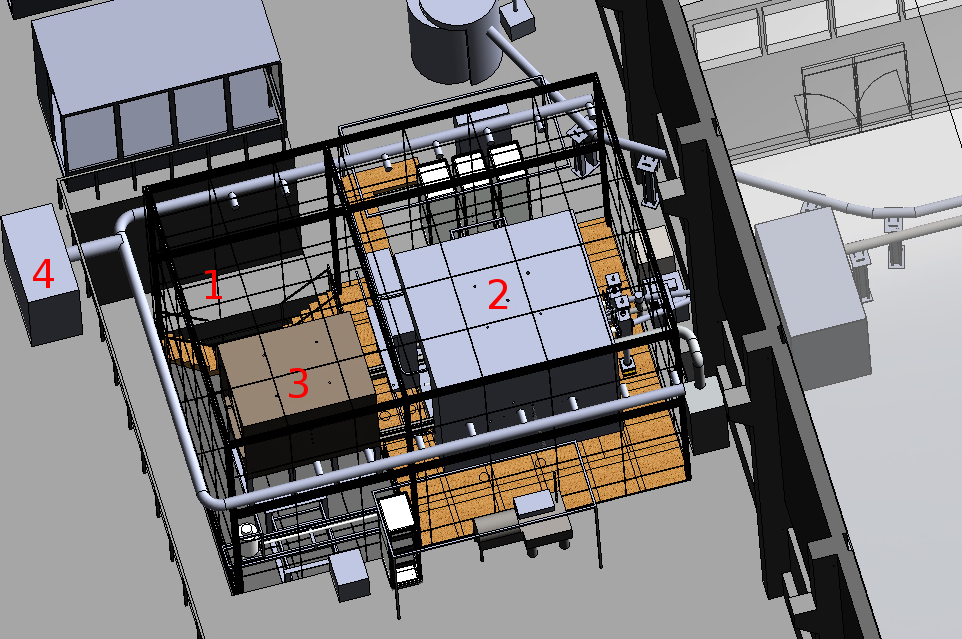
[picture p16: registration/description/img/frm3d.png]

\caption{Experiment Umgebung. 1: Spulenkäfig zur magnetischen Feldkompensation,
2: Äußeres magnetisches Schild, 3: Inneres magnetisches Schild, 4: Klimaanlage}
\label{fig:exp}
\end{figure}
\subsection*{Notwendigkeit der Umgebungsmessung}
Um sicher zu stellen, dass bei dem Experiment konstante Bedingungen herrschen
ist neben der exakt definierten magnetischen Umgebung auch die 
Umgebungstemperatur, sowie die Luftfeuchtigkeit innerhalb des äußeren
Spulenkäfigs von großer Wichtigkeit. Diese wird von einer Klimaanlage
kontrolliert. Zur Steuer\-ung dieser Anlage muss jedoch die Tempera\-tur an
verschiedenen Positionen im Spulenkäfig gemessen werden.
\section*{Die Vorlesung ``Particle Physics with Neutrons''}
Die Vorlesung behandelt Grundlagen der Neutronenphysik. Sie gibt insbesondere
einen Überblick über die Physik der ultrakalten Neutronen, sowie über einige
experimentelle Methoden im Kontext von Neutronen.\\
Die Vorlesung erlaubt es uns somit, die Hintergründe des nEDM Experiments zu
verstehen, was für die Entwicklung eines Sensornetzwerkes von höchster
Wichtigkeit ist, um die Anforderungen an das Messsystem genau abschätzen zu
können (Genauigkeit, Störungen, Zuverlässigkeit, etc.).
\section*{Unser Projekt}
\subsection*{Überblick}
Das Ziel des Projekts ist Aufbau eines Temperatur- und Luftfeuchtigkeit-
Sensornetzwerks innerhalb des Spulenkäfigs. Die gemessene Temperatur- und 
Luft\-feuchtig\-keits-Daten sollen im JSON Format per Ethernet geschickt werden, um 
die Klimaanlagen zu regeln, und zudem in einer 
Datenbank gespeichert werden, zur späteren Korrektur der nEDM Messungen. 
Die voraus\-sichtlich gewünschten Genauig\-keiten sind in Tabelle \ref{tab:genauigkeit} gelistet.
Unser Projekt unterteilt sich in folgende Teilaufgaben:
\begin{itemize}
\item Recherche nach passenden Sensoren 
\item Auslesen der Sensor-Daten
\item Formatierung der Messwerte
\item Datenübertragung per Ethernet
\item Installation des Sensornetzwerks im Experimentaufbau
\item Schreiben einer Dokumentation
\end{itemize}
\begin{table}[h]
  \centering
  \begin{tabular}{|l|c|}
    \hline
    Temperatur-Genauigkeit & $\pm0.1 K$
    \\ \hline
    Luftfeuchtigkeits-Genauigkeit & $\pm 2\%RH$
    \\ \hline
    Daten Übertragungsfrequenz & $\approx 1Hz$
    \\ \hline
  \end{tabular}
  \caption{Voraussichtliche Genauigkeiten}
  \label{tab:genauigkeit}
\end{table}
\subsection*{Meilensteine}
Der vorgesehene Zeitplan und Aufgabenaufteilung ist in folgender Grafik dargestellt:
\begin{center}

\end{center}
\end{document}

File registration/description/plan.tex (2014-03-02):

\documentclass[paper=a4, fontsize=11pt]{article}
\usepackage{tikz}
\usepackage{siunitx}
\usepackage{pgfplots}
\usepackage{kpfonts}
\usetikzlibrary{shapes, arrows, backgrounds,snakes, positioning}
\usepackage[graphics,tightpage,active]{preview}
\PreviewEnvironment{tikzpicture}
\PreviewEnvironment{equation}
\PreviewEnvironment{equation*}
\newlength{\imagewidth}
\newlength{\imagescale}
\pagestyle{empty}
\thispagestyle{empty}
\title{Plan}
\author{Wenwen Chen}
\date{\normalsize\today}
% These set the width of column and the height of month.
\newcommand{\colWidth}{7cm}
\newcommand{\monthHeight}{4em}
\newcommand{\monthLength}{1.5}
\newcommand{\titleHeight}{2.5}
\newcommand{\leftWidth}{1}
\begin{document}
\tikzset{entry/.style 2 args={
    draw=pgftransparent!0,
    line width=4pt,
    font=\sffamily,
    rectangle,
    rounded corners,
    fill=black!10,
    anchor=north west,
    inner sep=0.2333em,
    text width={\colWidth/#2-1.2em-1.6pt},
    minimum height=#1*\monthHeight,
    align=center
}}
\tikzset{entry1/.style 2 args={
    %xshift=(0.5334em+0.8pt)/2,
    draw=pgftransparent!0,
    line width=4pt,
    font=\sffamily,
    rectangle,
    rounded corners,
    fill=blue!40,
    anchor=north west,
    inner sep=0.2333em,
    text width={\colWidth/#2-1.2em-1.6pt},
    minimum height=#1*\monthHeight,
    align=center
}}
\tikzset{entry2/.style 2 args={
    %xshift=(0.5334em+0.8pt)/2,
    draw=pgftransparent!0,
    line width=4pt,
    font=\sffamily,
    rectangle,
    rounded corners,
    fill=green!30,
    anchor=north west,
    inner sep=0.2333em,
    text width={\colWidth/#2-1.2em-1.6pt},
    minimum height=#1*\monthHeight,
    align=center
}}
\begin{tikzpicture}[y=-\monthHeight,x=\colWidth]

    % First print a list of times.
    \foreach \number/\month in {1.8/2014,2/Feb.,3/Mar.,4/Apr.,5/Mai,6/Jun.,7/Jul.,8/Aug.,9/Sep.}
        \node[anchor=north east] at (\leftWidth,\number*\monthLength) {\month};

    % Draw some day dividers.
		\def\sL{14}
    \draw (\leftWidth-0.01,\titleHeight) -- (\leftWidth-0.01,-\sL*\monthHeight);
		\draw[dashed] (2-0.01,\titleHeight) -- (2-0.01,-\sL*\monthHeight);
    \draw (3-0.01,\titleHeight) -- (3-0.01,-\sL*\monthHeight);
	
		\def\lP{0.85}
		\draw[dashed] (\lP,2*\monthLength+0.07) -- (3+0.01,2*\monthLength+0.07);
		\draw[dashed] (\lP,3*\monthLength+0.07) -- (3+0.01,3*\monthLength+0.07);
		\draw[dashed] (\lP,4*\monthLength+0.07) -- (3+0.01,4*\monthLength+0.07);
		\draw[dashed] (\lP,5*\monthLength+0.07) -- (3+0.01,5*\monthLength+0.07);
		\draw[dashed] (\lP,6*\monthLength+0.07) -- (3+0.01,6*\monthLength+0.07);
		\draw[dashed] (\lP,7*\monthLength+0.07) -- (3+0.01,7*\monthLength+0.07);
		\draw[dashed] (\lP,8*\monthLength+0.07) -- (3+0.01,8*\monthLength+0.07);
		\draw[dashed] (\lP,9*\monthLength+0.07) -- (3+0.01,9*\monthLength+0.07);

    % Start Monday.
    \node[anchor=north] at (1.5,\titleHeight) {Rainer Schoenberger};
    % Write the entries. Note that the x coordinate is 1 (for Monday) plus an
    % appropriate amount of shifting. The y coordinate is simply the starting
    % time.
		\def\mouthL{\monthLength}
    \node[entry={0.4*\mouthL}{0.5}] at (1, 2.7*\mouthL) {Get to know more about experiment};
    \node[entry1={0.4*\mouthL}{1}] at (1, 3.10*\mouthL) {Search Temperature sensor};
    \node[entry={0.4*\mouthL}{0.5}] at (1, 3.50*\mouthL) {Design protocol and Interface};
    \node[entry1={1*\mouthL}{1}] at (1, 3.9*\mouthL) {Read sensor data};
    \node[entry1={0.5*\mouthL}{1}] at (1, 4.9*\mouthL) {Test sensor communication};
    \node[entry1={0.4*\mouthL}{1}] at (1, 5.4*\mouthL) {Construct sensor casing and mounting};
    \node[entry={0.7*\mouthL}{0.5}] at (1, 5.8*\mouthL) {Integration and Test};
    \node[entry={1*\mouthL}{0.5}] at (1, 6.5*\mouthL) {Dokumentation};
    \node[entry={0.3*\mouthL}{0.5}] at (1, 7.5*\mouthL) {Presentation};
    \node[entry={1*\mouthL}{0.5}] at (1, 7.8*\mouthL) {Buffer};

    % The same for Tuesday.
    \node[anchor=north] at (2.5,\titleHeight) {Wenwen Chen};
    \node[entry2={0.4*\mouthL}{1}] at (2.0,3.1*\mouthL) {Search humidity sensor};
    \node[entry2={1*\mouthL}{1}] at (2.0,3.9*\mouthL) {Datatransfer via Ethernet};
    \node[entry2={0.4*\mouthL}{1}] at (2,4.9*\mouthL) {Design sensor casing and mounting};
    \node[entry2={0.5*\mouthL}{1}] at (2,5.3*\mouthL) {Test ethernet communication};
\end{tikzpicture}
\end{document}

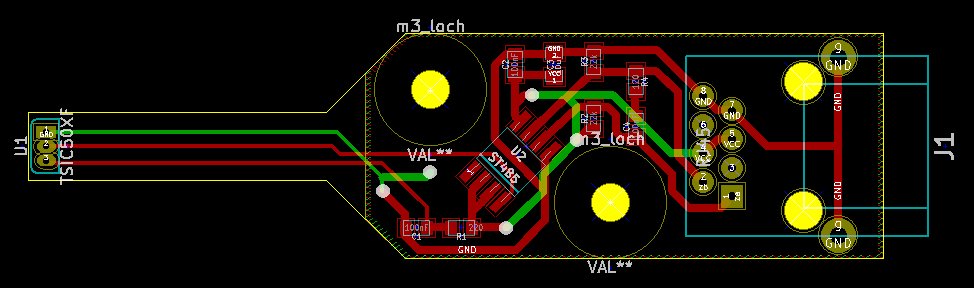
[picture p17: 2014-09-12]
report/img/boards/temp_kicad.jpg

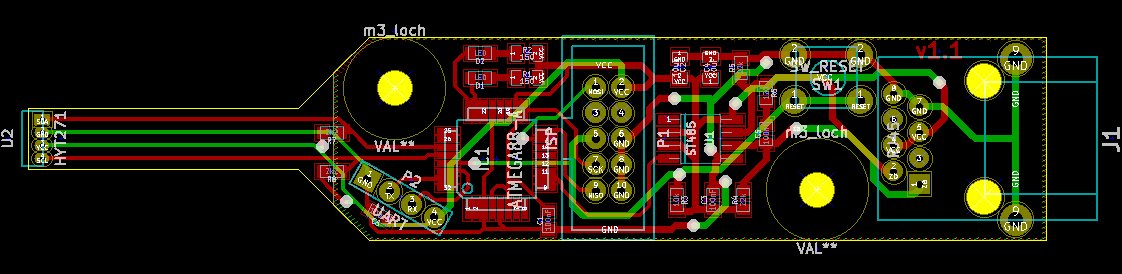
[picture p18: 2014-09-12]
report/img/boards/hum_kicad.jpg

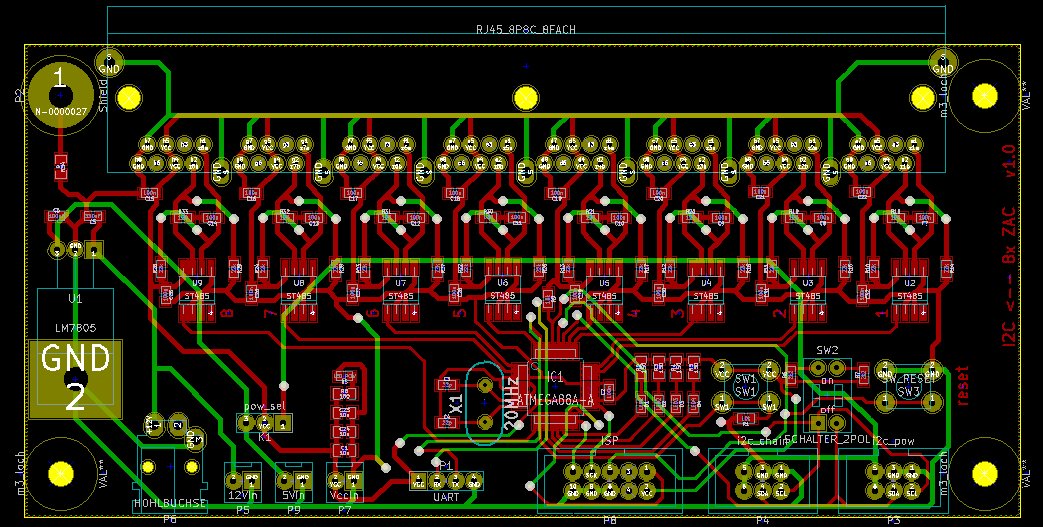
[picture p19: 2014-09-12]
report/img/boards/collector_kicad.jpg

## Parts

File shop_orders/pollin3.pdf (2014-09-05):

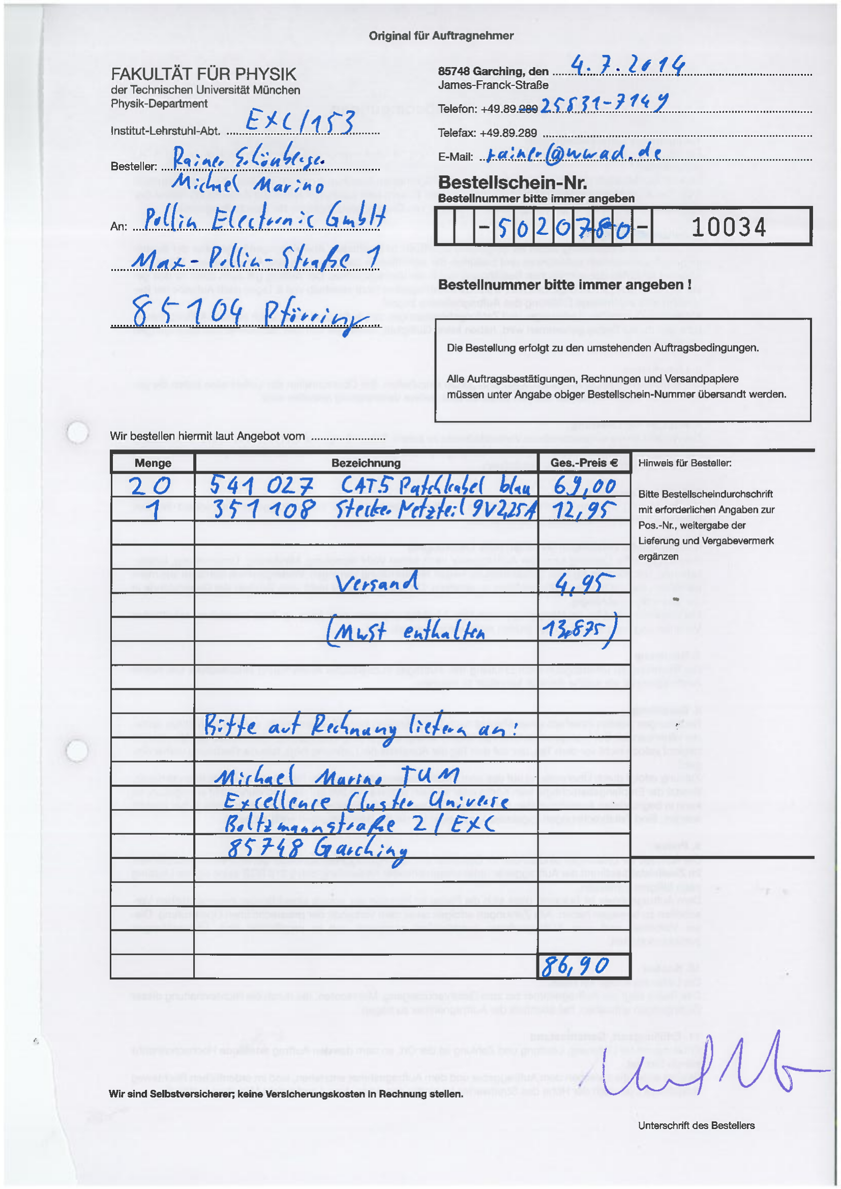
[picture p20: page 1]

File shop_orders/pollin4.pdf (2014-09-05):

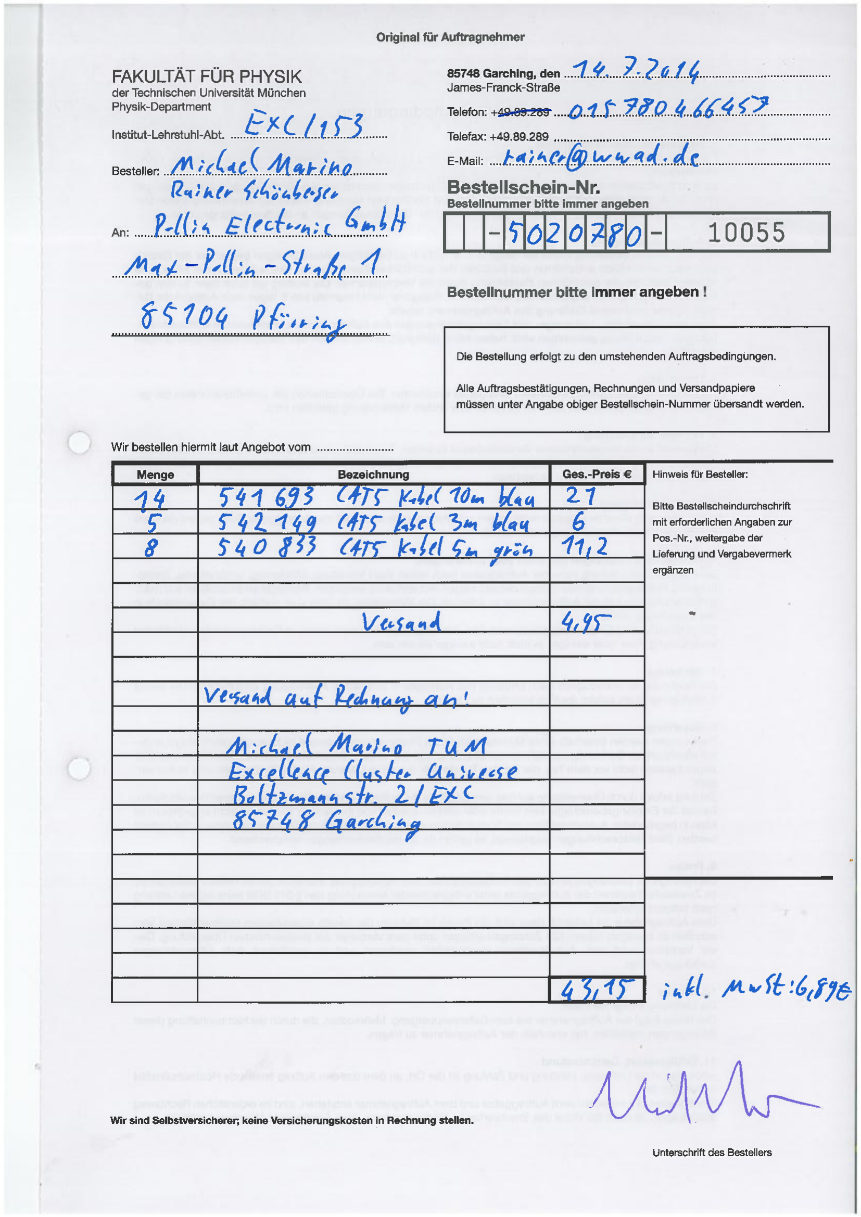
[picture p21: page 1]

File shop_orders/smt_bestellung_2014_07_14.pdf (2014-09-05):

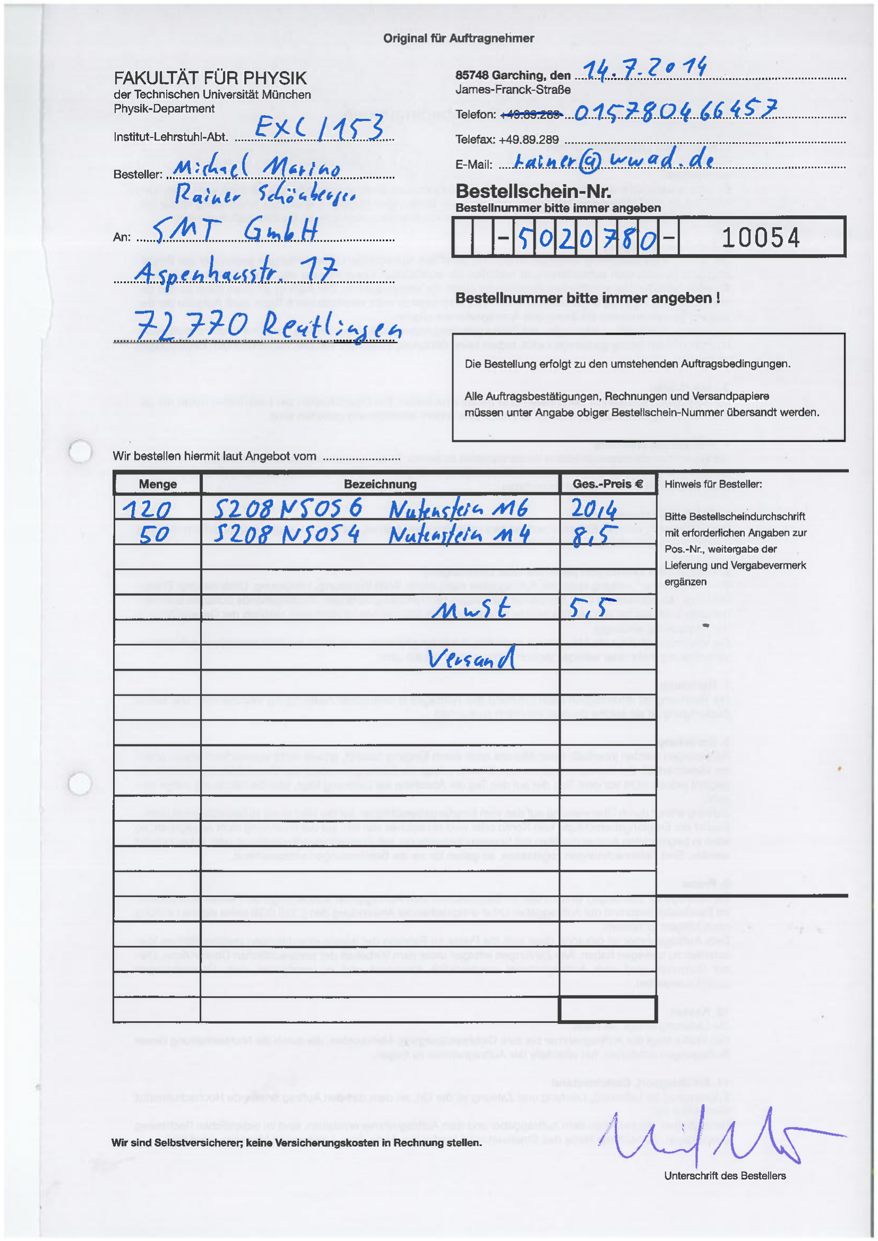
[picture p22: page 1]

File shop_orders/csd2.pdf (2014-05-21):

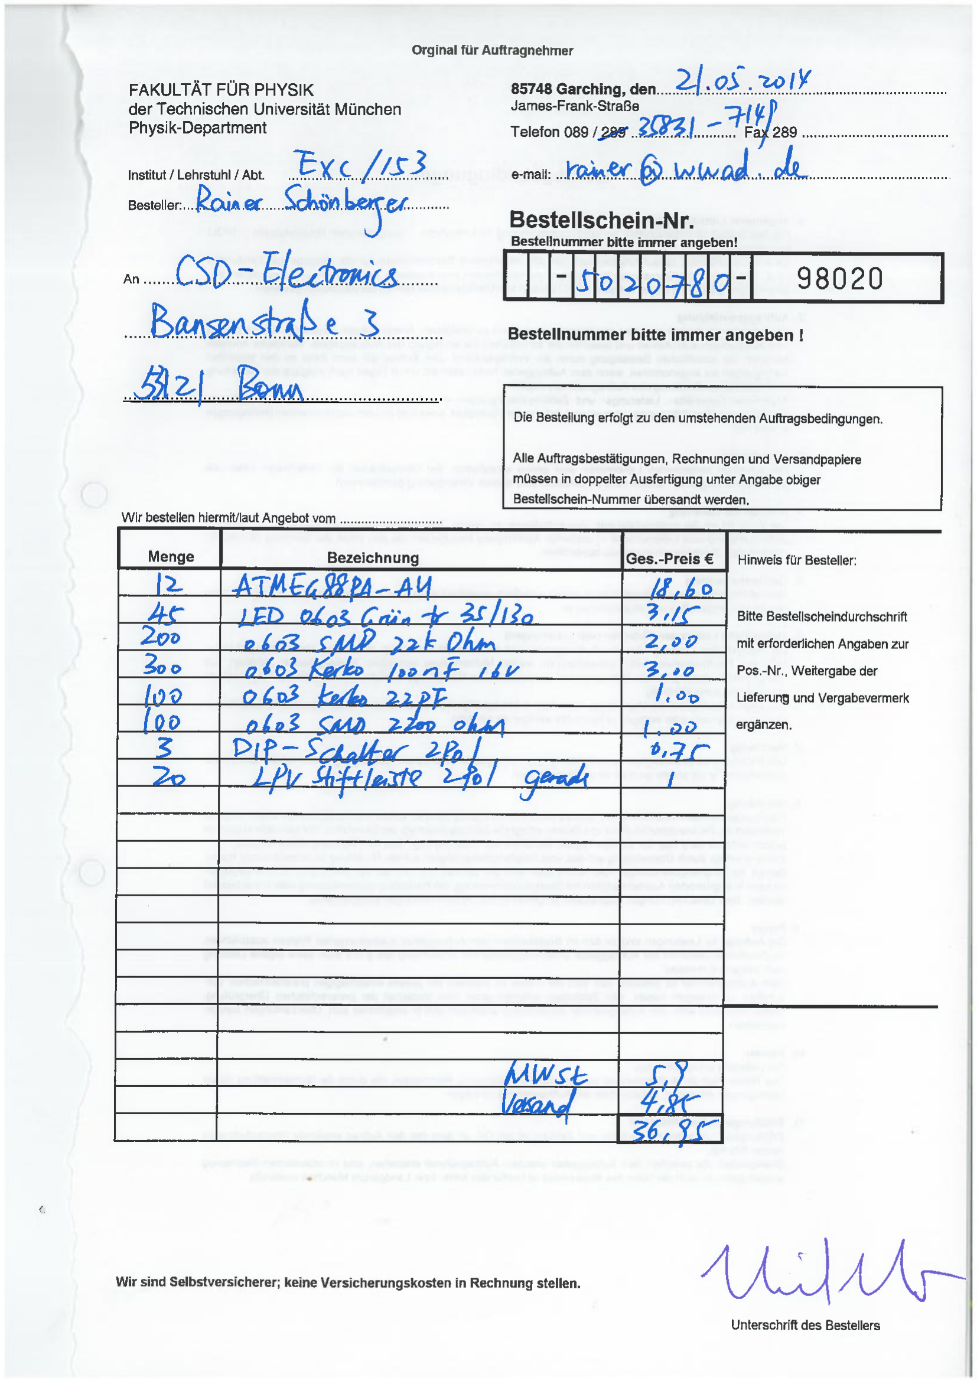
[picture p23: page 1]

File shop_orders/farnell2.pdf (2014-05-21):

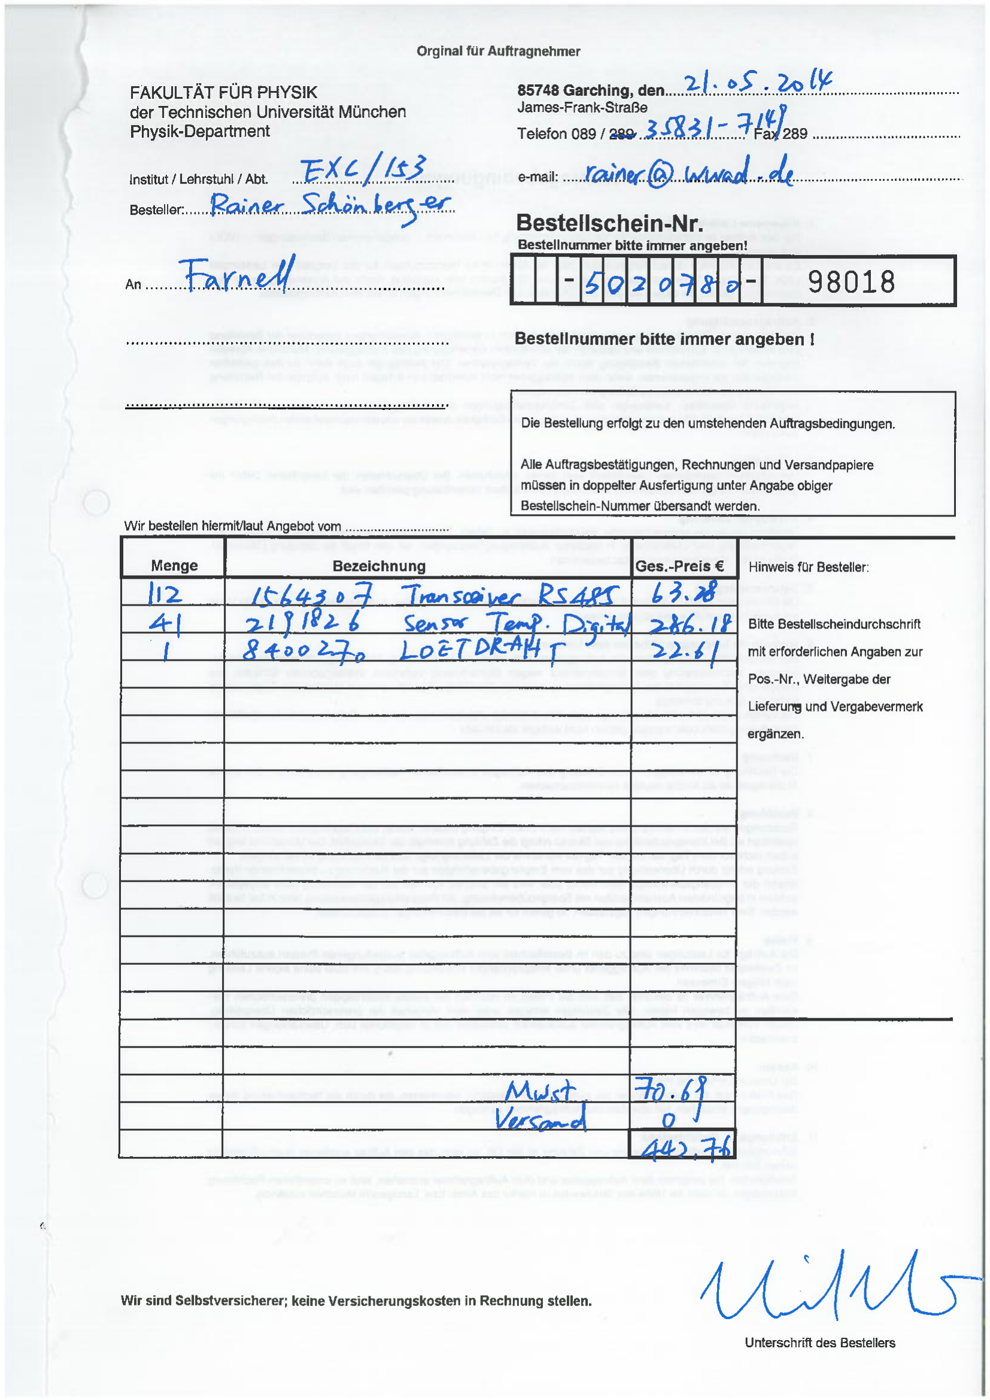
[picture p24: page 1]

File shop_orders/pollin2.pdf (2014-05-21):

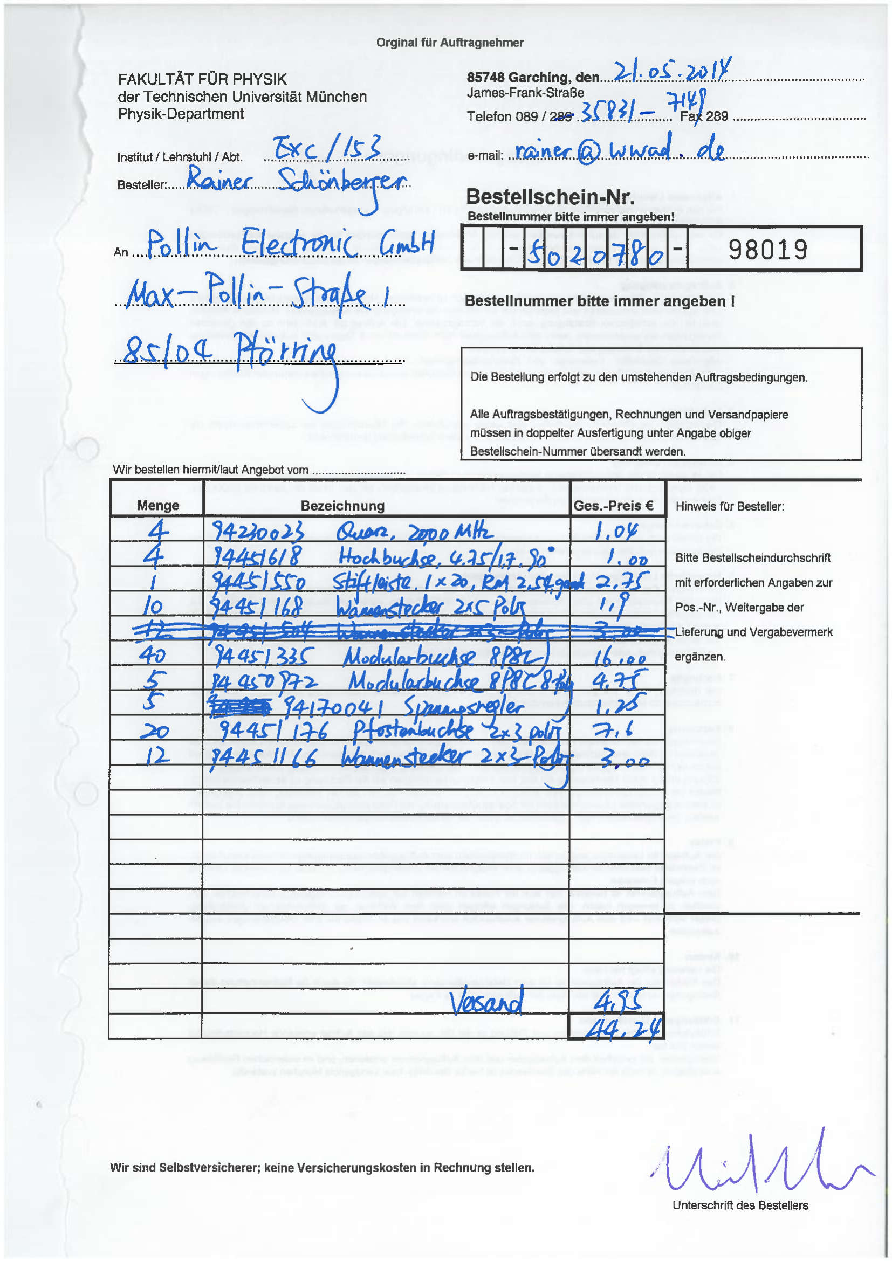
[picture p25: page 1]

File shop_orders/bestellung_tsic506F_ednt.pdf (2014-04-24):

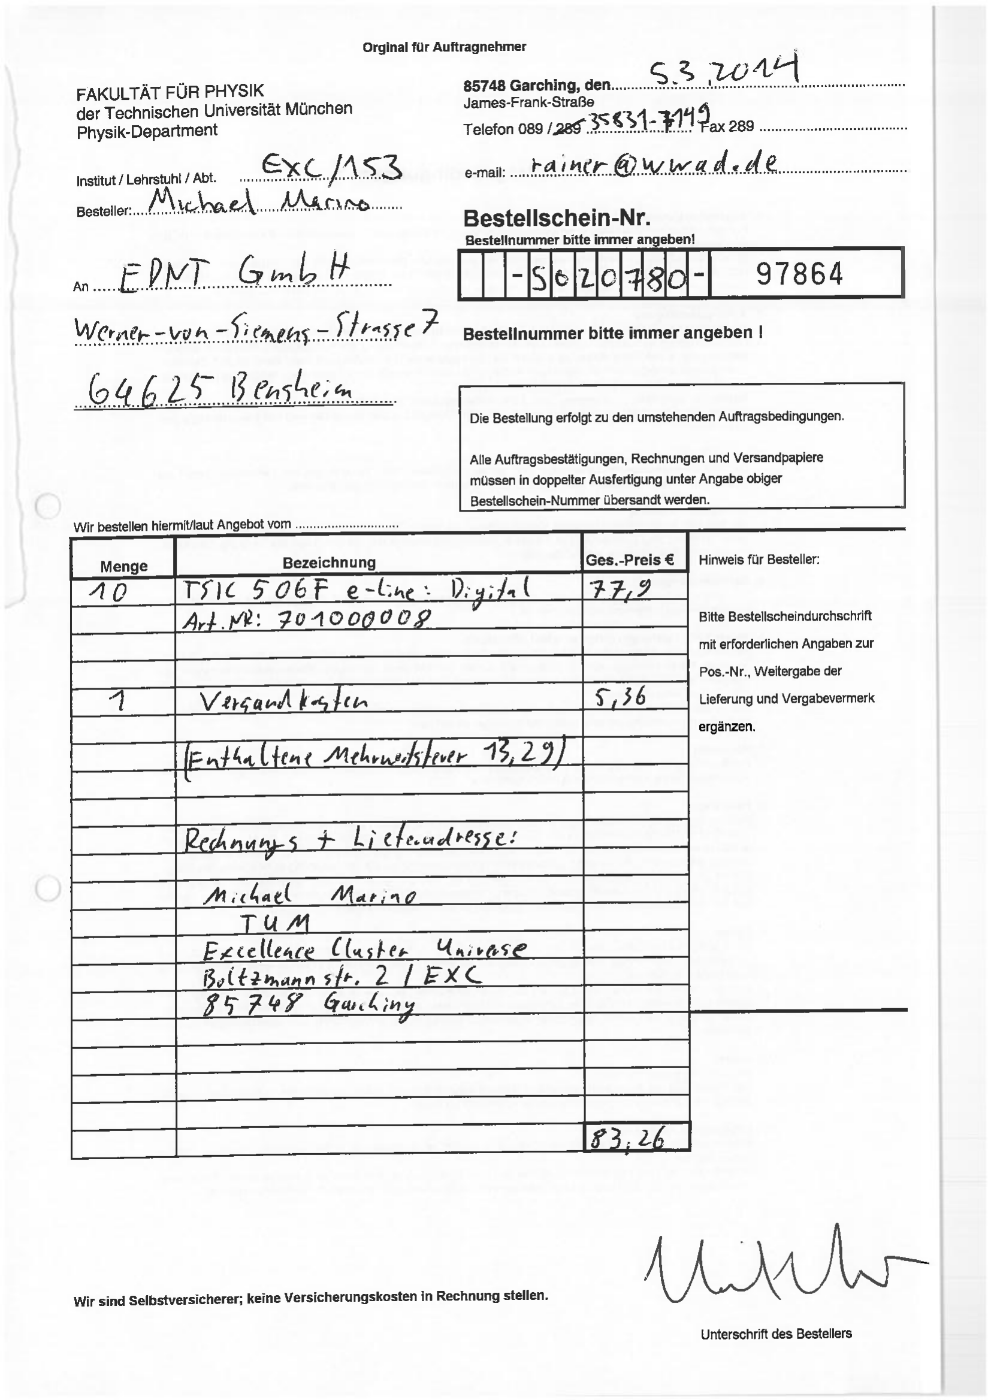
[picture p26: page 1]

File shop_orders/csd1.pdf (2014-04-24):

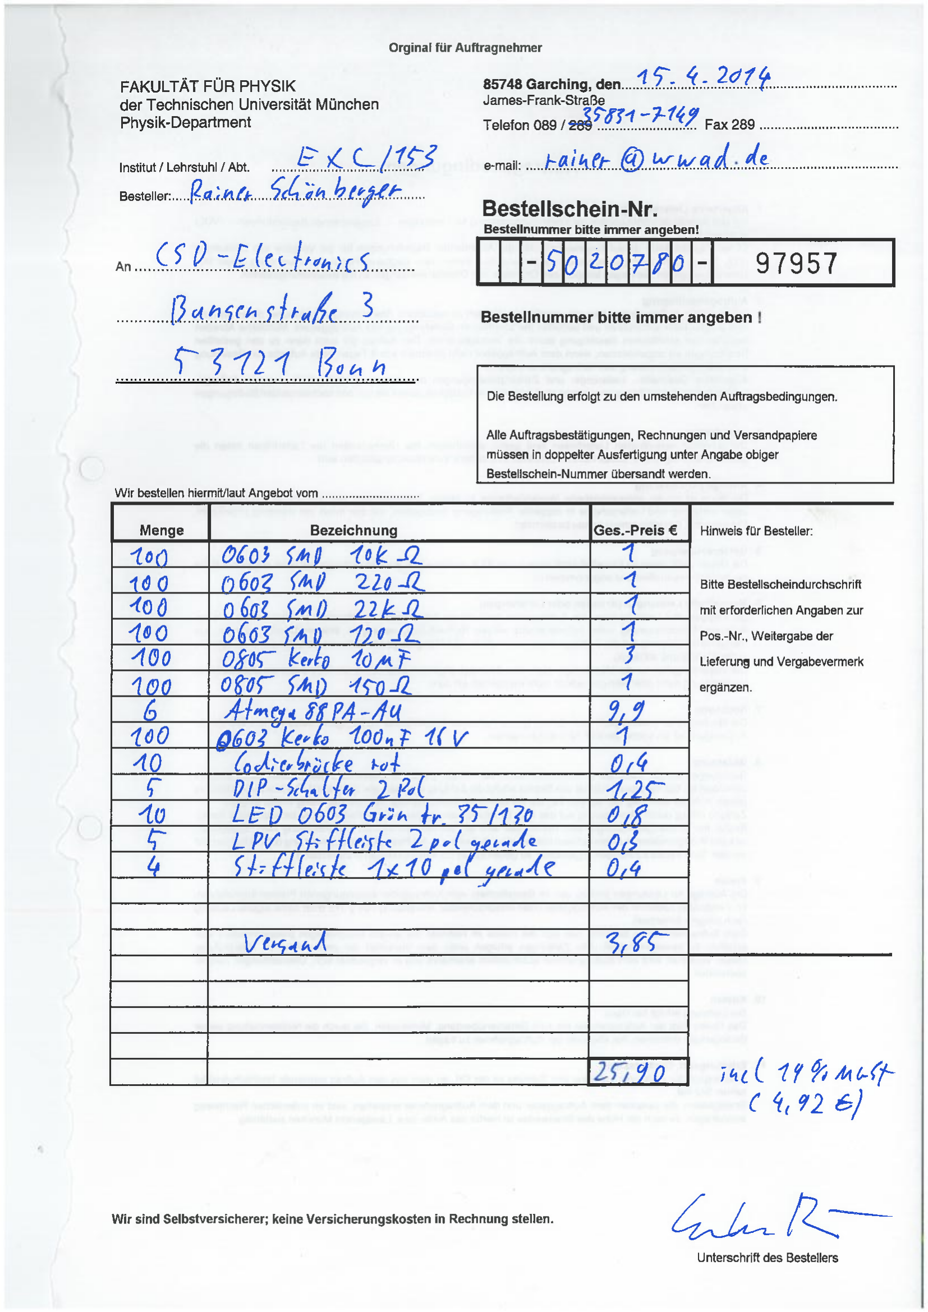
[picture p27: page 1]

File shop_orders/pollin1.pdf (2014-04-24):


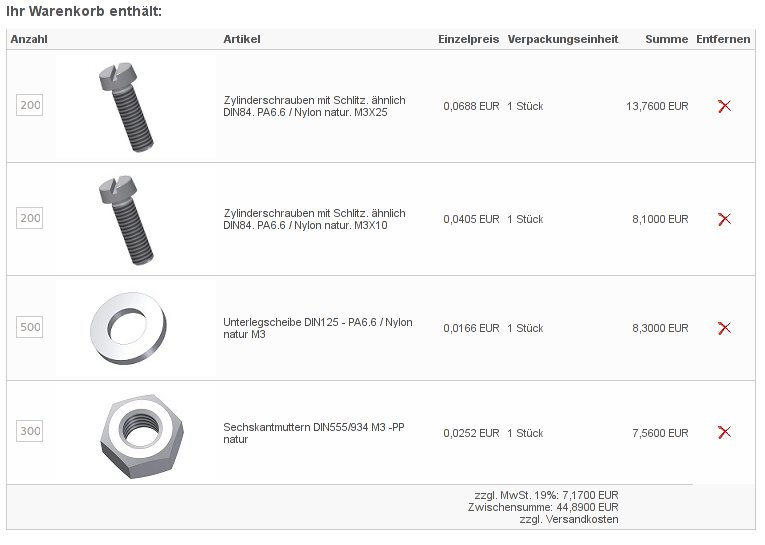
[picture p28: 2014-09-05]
shop_orders/planschrauben.jpg

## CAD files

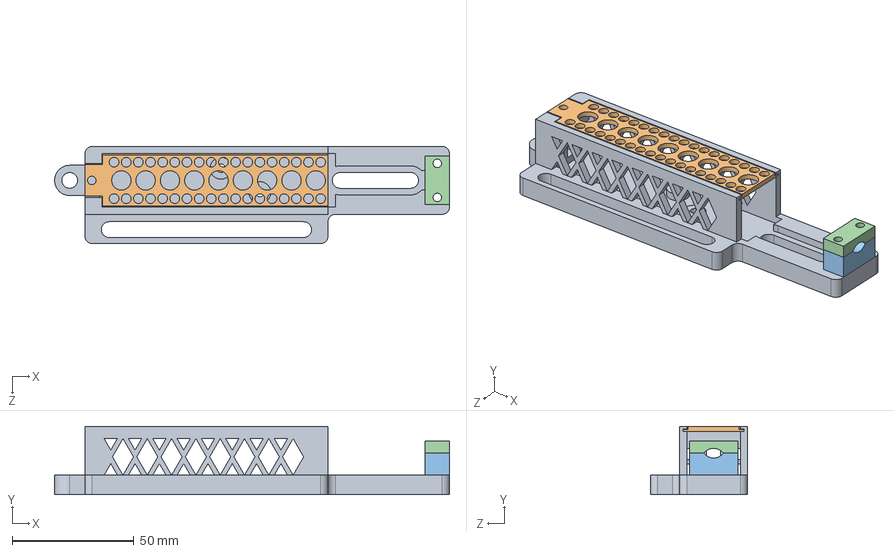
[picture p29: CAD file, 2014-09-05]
casings/temperature/temp_housing.SLDASM
162.5 x 28.0 x 40.0 mm
temp_base
temp_lid
hum_cable-clamp1
hum_cable-clamp2

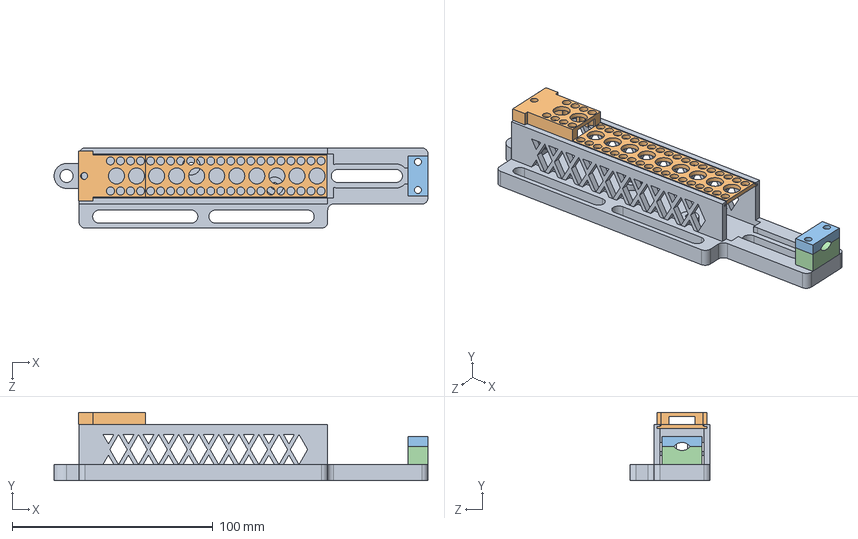
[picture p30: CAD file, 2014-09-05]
casings/humidity/hum_housing.SLDASM
186.5 x 34.0 x 40.0 mm
hum_base
hum_lid
hum_cable-clamp2
hum_cable-clamp1

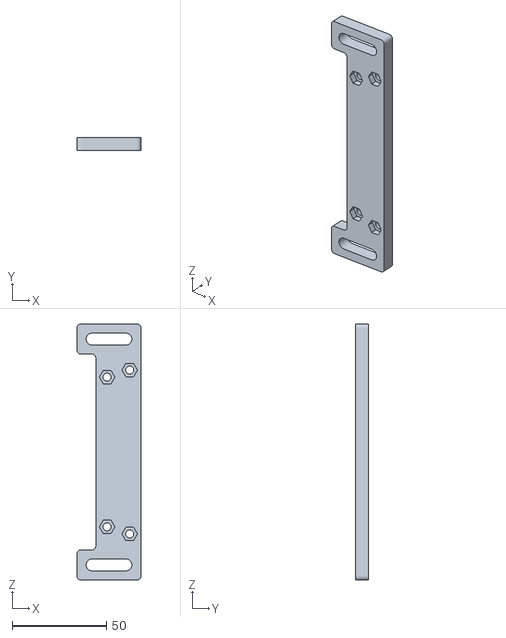
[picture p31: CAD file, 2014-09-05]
casings/adapter/adapter_finished_rounded_stl.stl
34.0 x 7.00 x 136.0

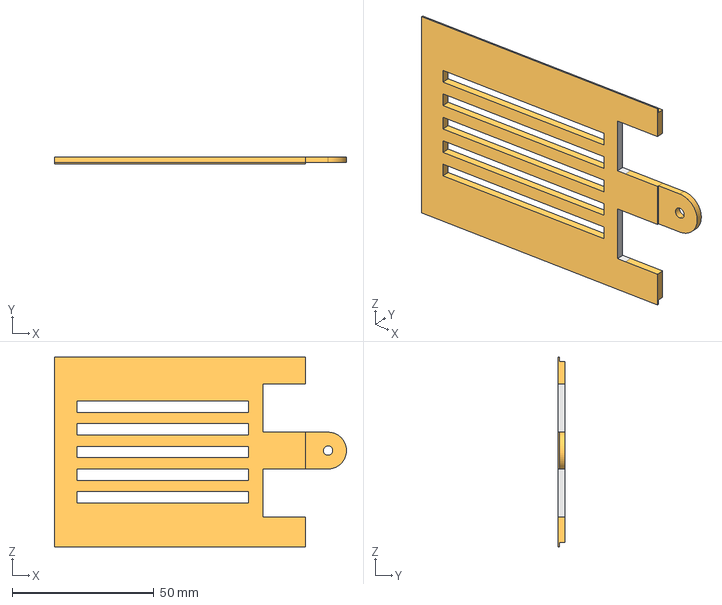
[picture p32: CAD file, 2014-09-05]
casings/arduino/arduino_lid.step
103.0 x 2.50 x 67.0 mm

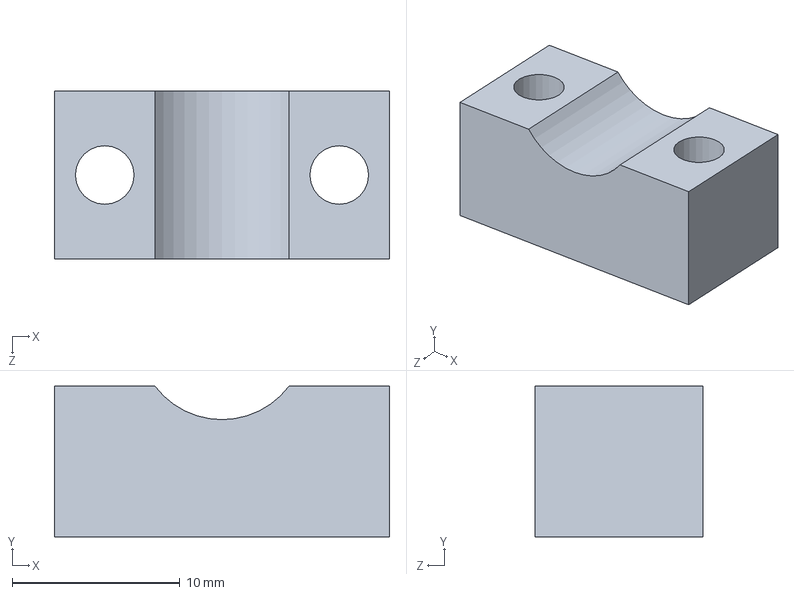
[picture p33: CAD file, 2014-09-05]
casings/cable_clamp/hum_cable-clamp1.SLDPRT
20.0 x 9.00 x 10.0 mm

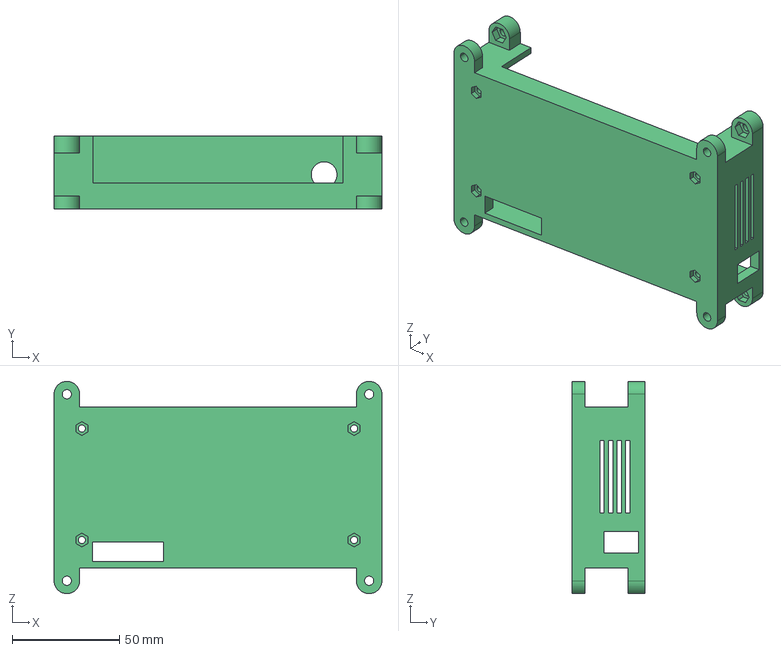
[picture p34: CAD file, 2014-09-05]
casings/collector/gehaeuse_1_SW5.stp
153.0 x 34.0 x 99.0 mm

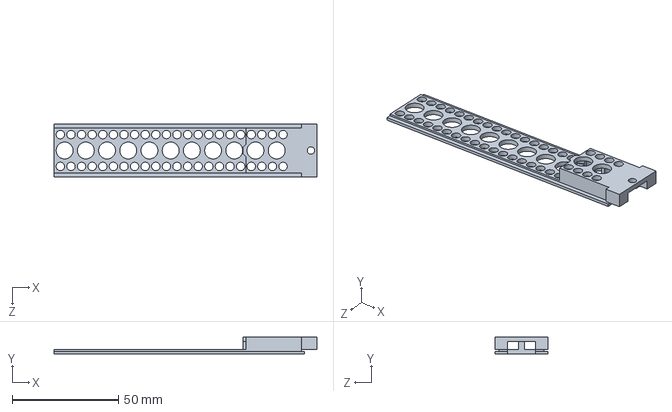
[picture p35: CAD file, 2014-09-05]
casings/humidity/hum_lid.SLDPRT
124.0 x 8.00 x 25.0 mm

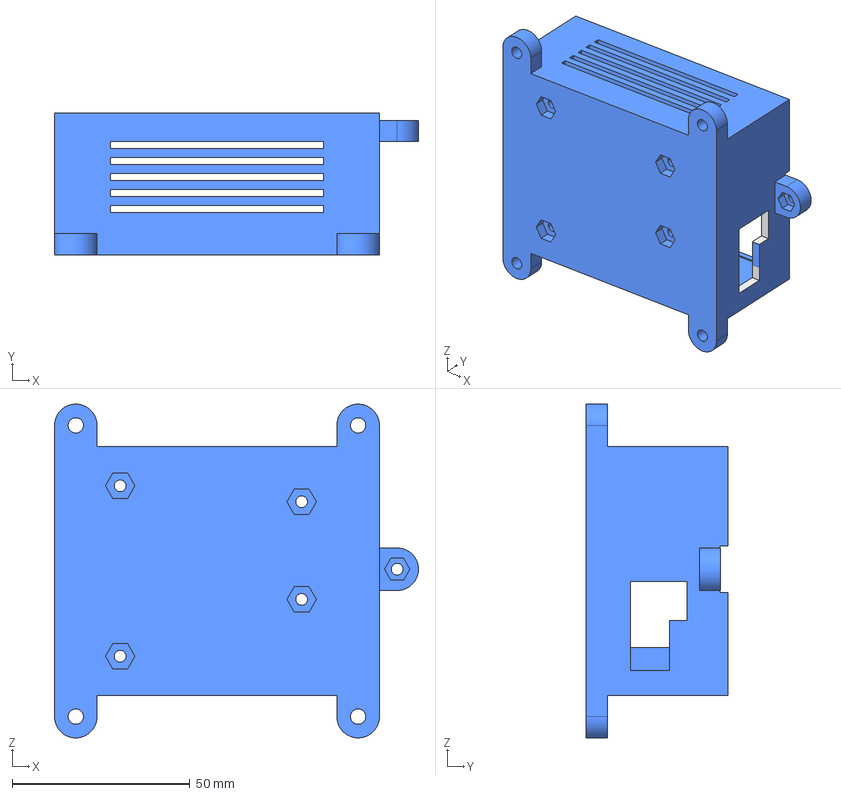
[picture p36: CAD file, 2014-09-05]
casings/arduino/arduino_body.step
102.5 x 40.0 x 94.0 mm

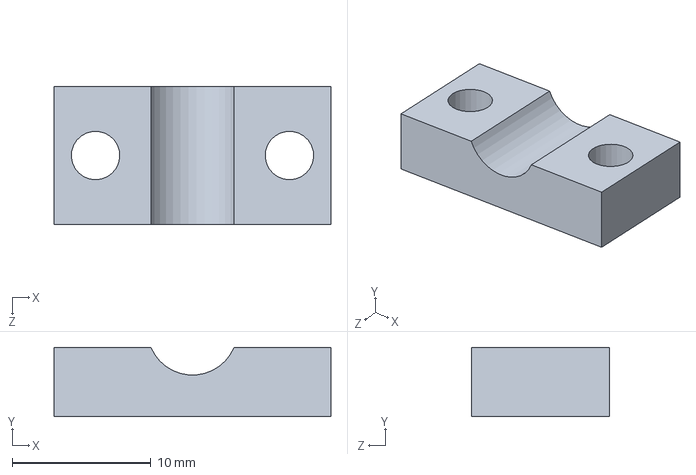
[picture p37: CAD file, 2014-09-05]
casings/cable_clamp/hum_cable-clamp.SLDPRT
20.0 x 5.00 x 10.0 mm

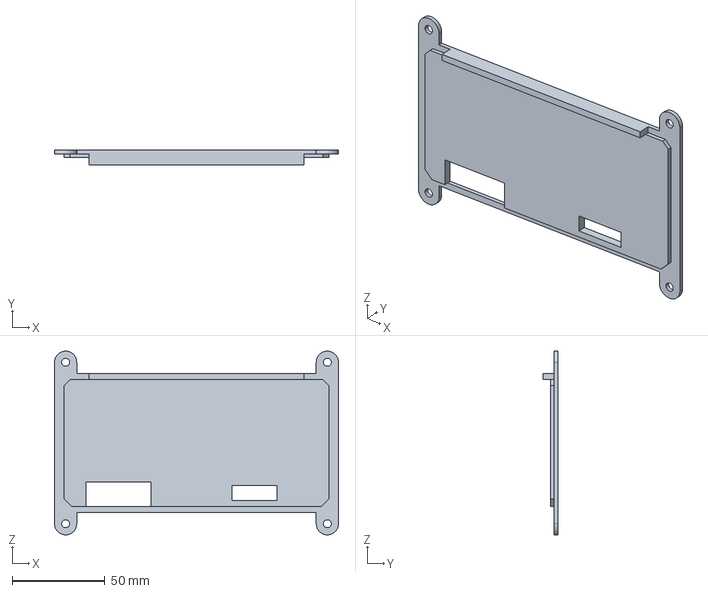
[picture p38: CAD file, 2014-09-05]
casings/collector/deckel_1.stp
153.0 x 8.00 x 99.0 mm

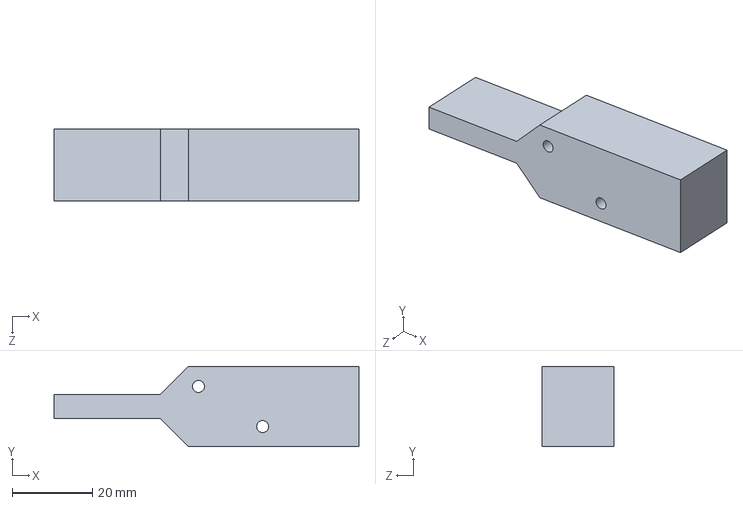
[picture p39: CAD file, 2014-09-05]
casings/temperature/temp.SLDPRT
76.0 x 20.0 x 18.0 mm

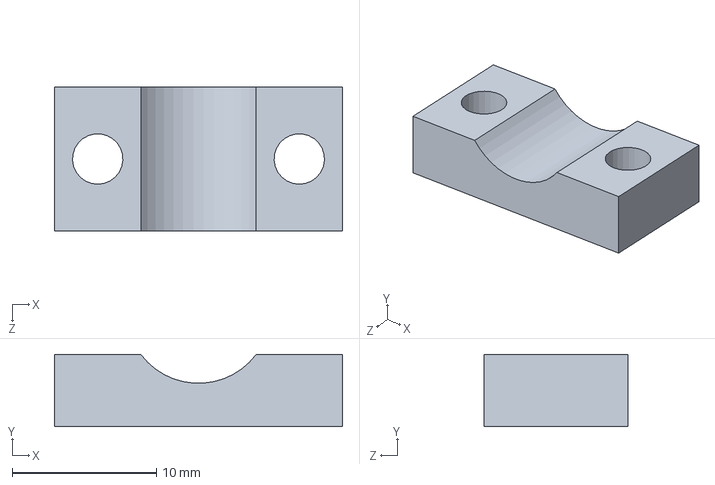
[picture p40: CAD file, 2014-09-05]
casings/cable_clamp/hum_cable-clamp2.SLDPRT
20.0 x 5.00 x 10.0 mm

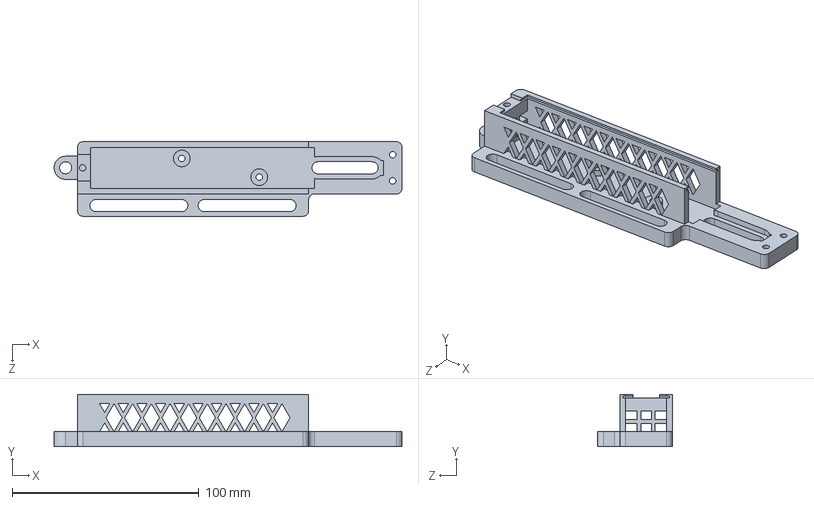
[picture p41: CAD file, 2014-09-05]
casings/humidity/hum_base.SLDPRT
186.5 x 28.0 x 40.0 mm

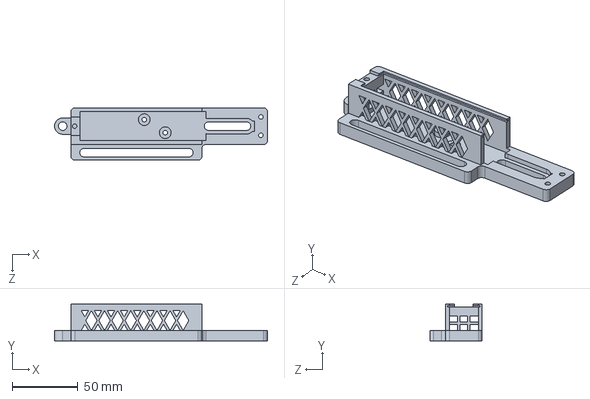
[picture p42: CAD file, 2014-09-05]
casings/temperature/temp_base.SLDPRT
162.5 x 28.0 x 40.0 mm

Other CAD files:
casings/adapter/finished_rounded_step.step
casings/humidity/hum_deckel.stl
casings/temperature/temp_lid.SLDPRT
casings/arduino/arduino_body.stl
casings/arduino/arduino_lid.stl

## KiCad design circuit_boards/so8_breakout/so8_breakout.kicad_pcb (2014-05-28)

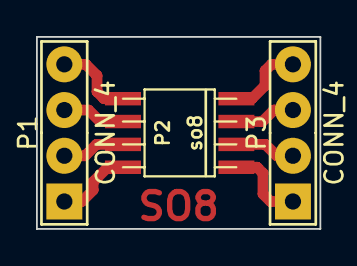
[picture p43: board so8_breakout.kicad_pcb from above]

Board: 2 copper layers, 15.7 x 10.7 mm, 3 parts (0 on the bottom side), 8 nets.

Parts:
P1, P3: CONN_4; Stiftleiste_4x1
P2: so8; st485

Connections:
unnamed: P1.3, P2.6
unnamed: P2.4, P3.4
unnamed: P2.3, P3.3
unnamed: P1.4, P2.5
unnamed: P1.2, P2.7
unnamed: P1.1, P2.8
unnamed: P2.2, P3.2
unnamed: P2.1, P3.1

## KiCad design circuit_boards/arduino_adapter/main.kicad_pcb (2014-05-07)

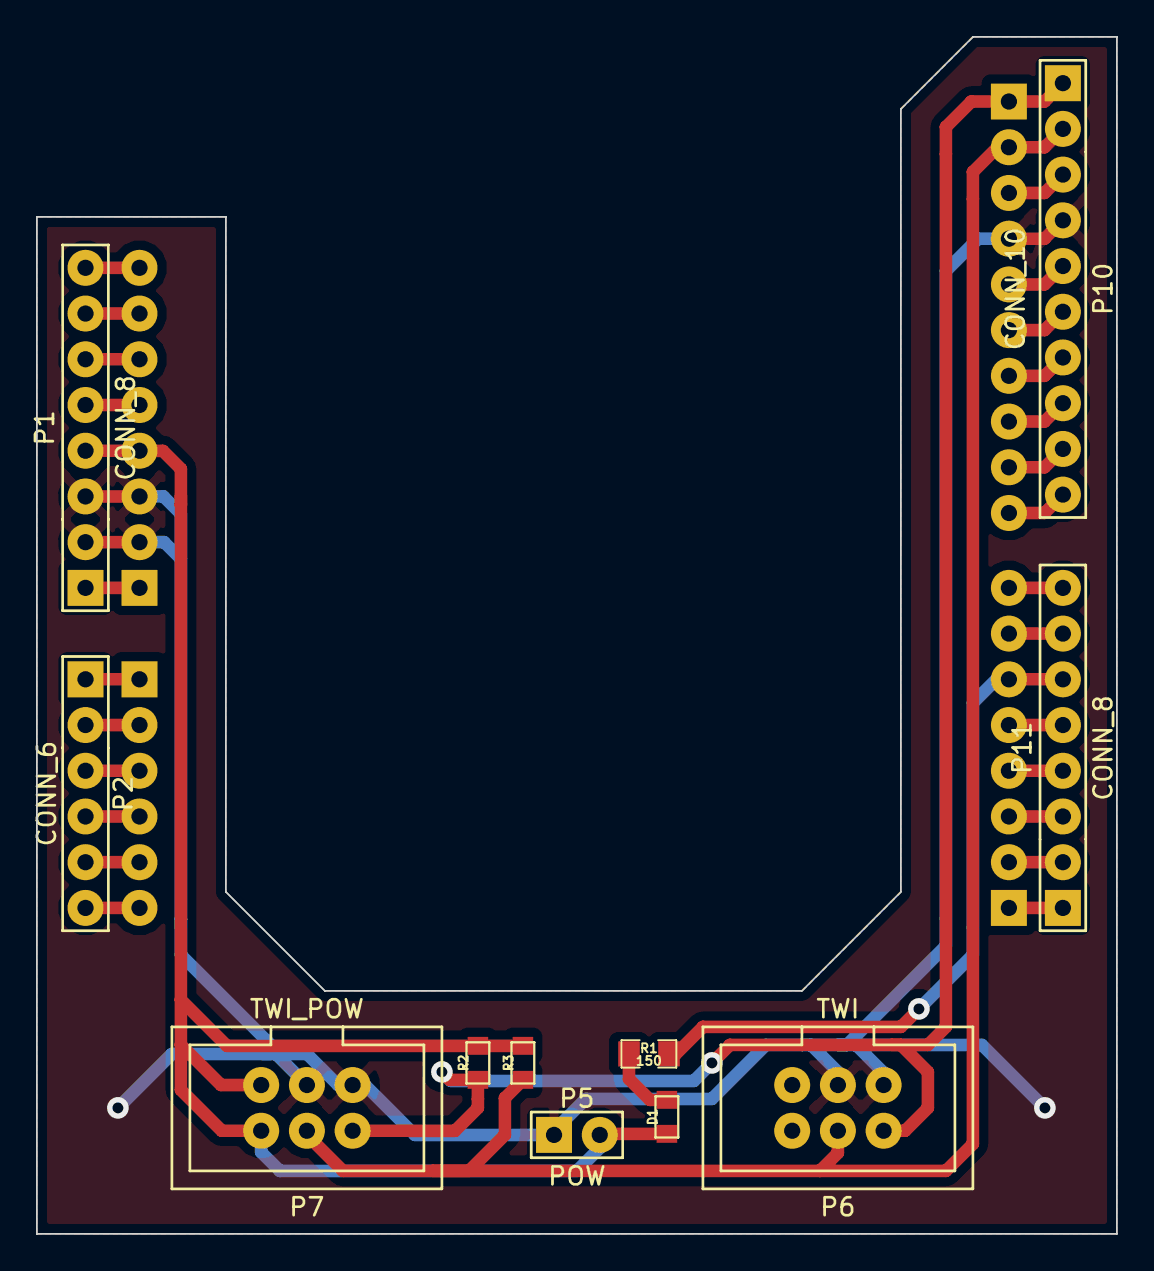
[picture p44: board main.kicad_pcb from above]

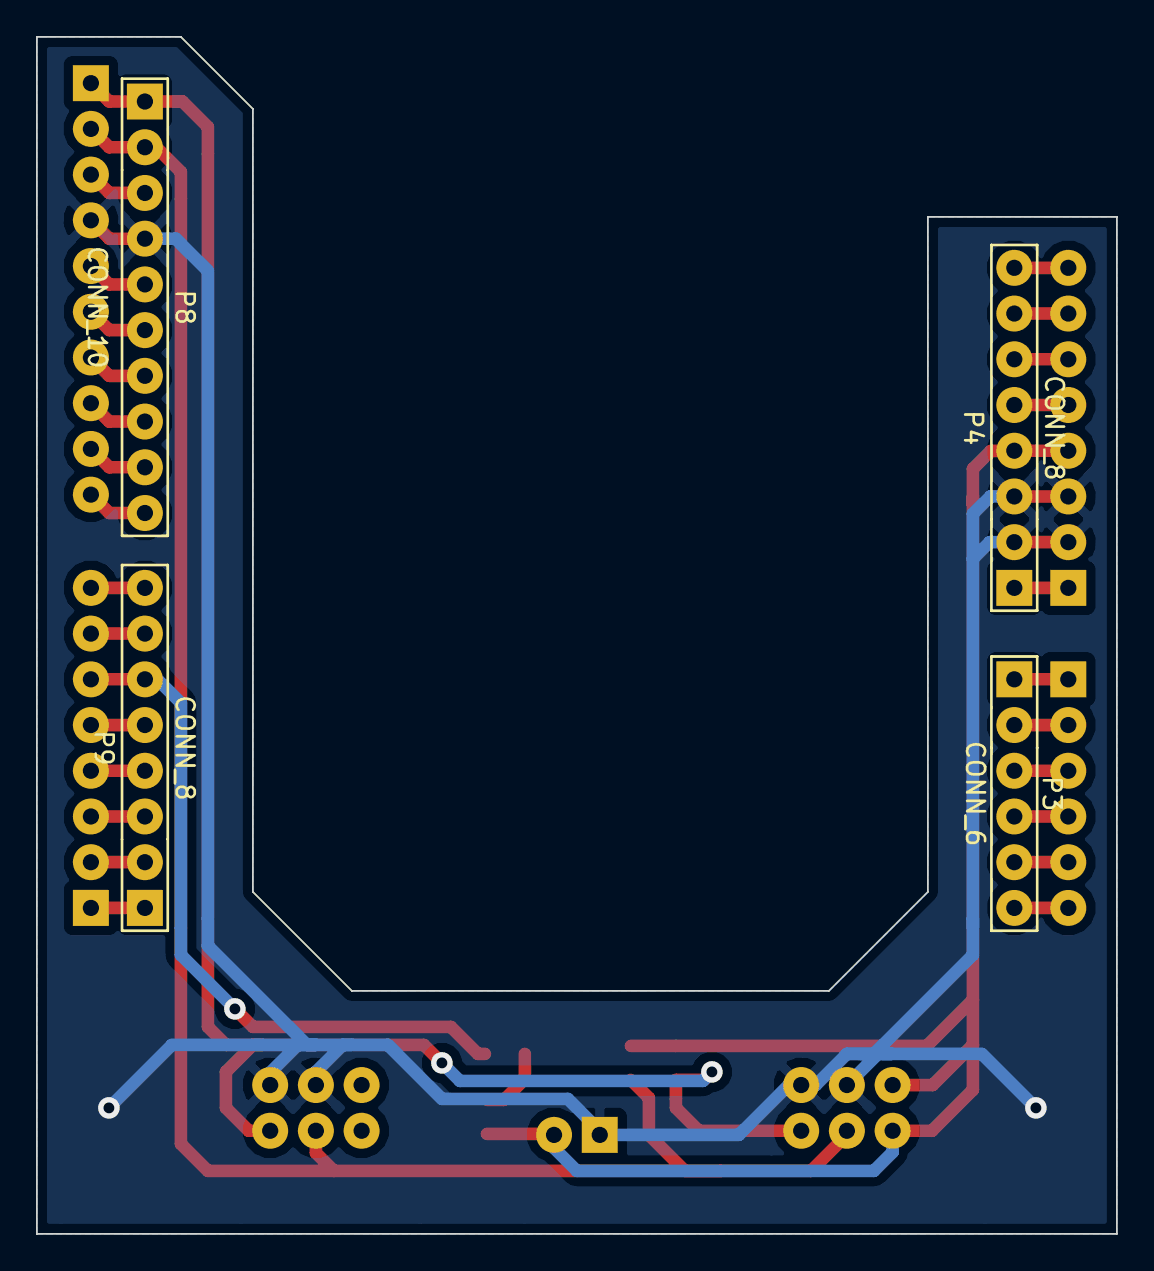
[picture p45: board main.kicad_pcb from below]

Board: 2 copper layers, 60.0 x 66.5 mm, 15 parts (4 on the bottom side), 31 nets.

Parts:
D1: LED; SM0603_big
P1, P4, P9, P11: CONN_8; Stiftleiste_8x1
P2, P3: CONN_6; Stiftleiste_6x1
P5: POW; Stiftleiste_2x1
P6: TWI; wannenstecker_2x3_rm254
P7: TWI_POW; wannenstecker_2x3_rm254
P8, P10: CONN_10; Stiftleiste_10x1
R1: 150; SM0805_big
R2, R3: 2k2; SM0603_big

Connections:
/LED: P9.6, P11.6, R1.2
/SCL: P6.2, P7.2, P8.1, P10.1, R2.1
/SDA: P6.4, P7.4, P8.2, P10.2, R3.1
GND: P1.2, P1.3, P4.2, P4.3, P5.1, P6.1, P6.3, P7.1, P7.3, P8.4, P10.4
unnamed: P1.1, P4.1
unnamed: P2.6, P3.6
unnamed: P2.5, P3.5
unnamed: P2.4, P3.4
unnamed: P2.3, P3.3
unnamed: P2.2, P3.2
unnamed: P2.1, P3.1
unnamed: P8.3, P10.3
unnamed: P8.5, P10.5
unnamed: P8.6, P10.6
unnamed: P8.7, P10.7
unnamed: P8.8, P10.8
unnamed: P8.9, P10.9
unnamed: P8.10, P10.10
unnamed: P9.1, P11.1
unnamed: P9.2, P11.2
unnamed: P9.3, P11.3
unnamed: P9.4, P11.4
unnamed: P9.5, P11.5
unnamed: P1.5, P4.5
unnamed: P1.6, P4.6
unnamed: P1.7, P4.7
unnamed: P1.8, P4.8
unnamed: P9.7, P11.7
unnamed: P9.8, P11.8
unnamed: D1.2, R1.1
VCC: D1.1, P1.4, P4.4, P5.2, P7.5, P7.6, R2.2, R3.2

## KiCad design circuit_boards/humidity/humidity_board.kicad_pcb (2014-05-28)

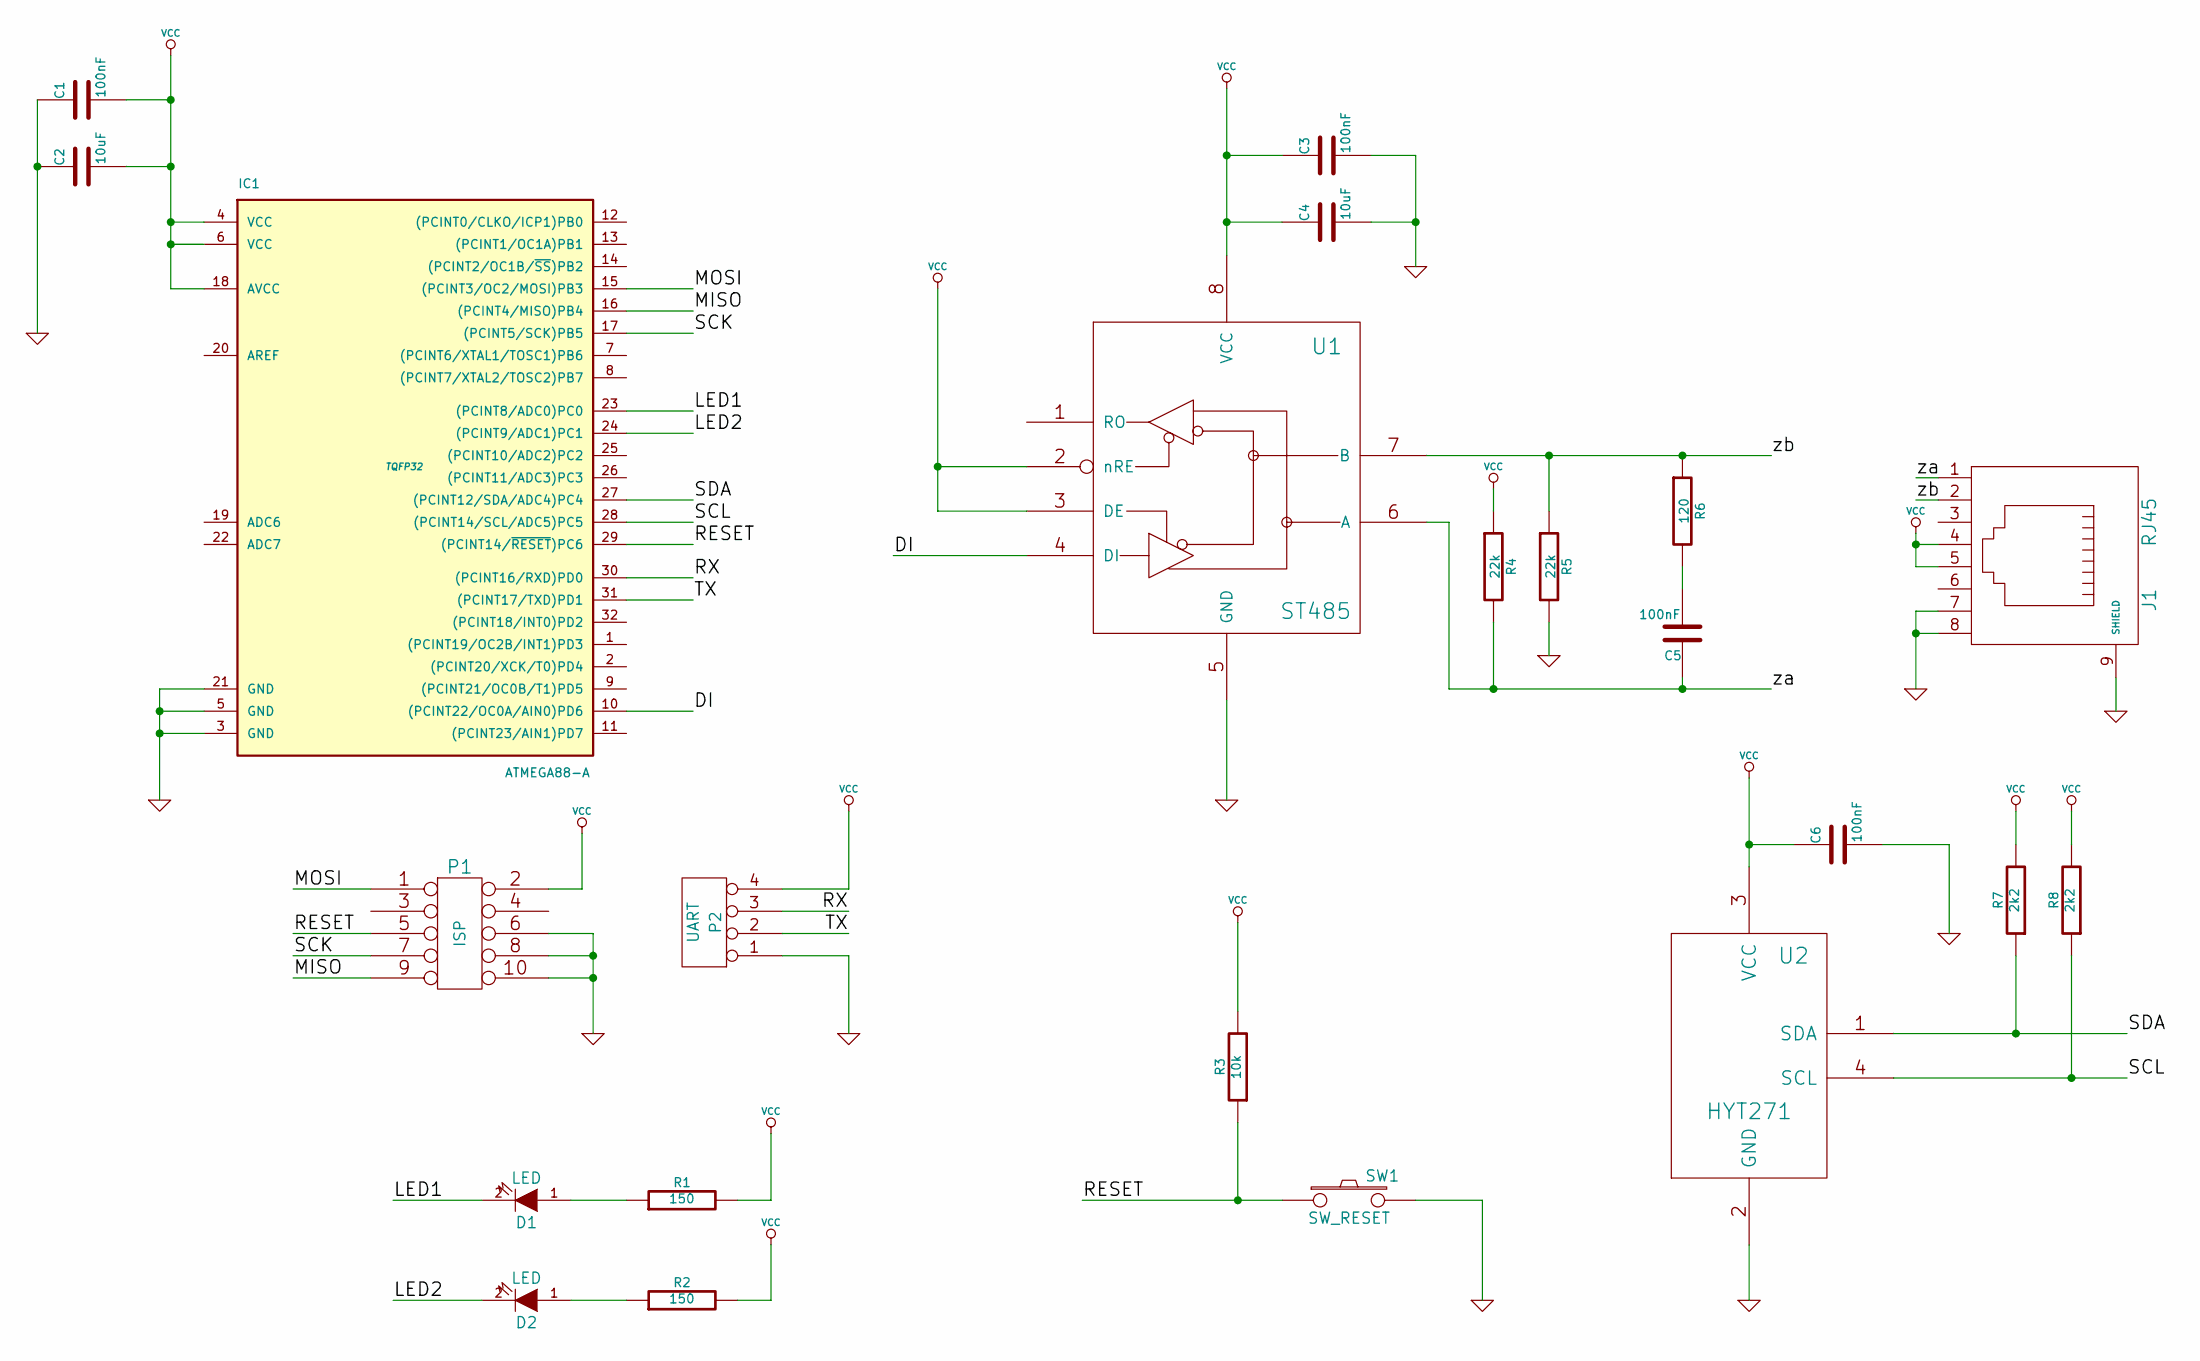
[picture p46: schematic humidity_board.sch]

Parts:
C1, C3, C5, C6: 100nF
C2, C4: 10uF
D1, D2: LED
IC1: ATMEGA88-A; TQFP32
J1: RJ45
P1: ISP
P2: UART
R1, R2: 150
R3: 10k
R4, R5: 22k
R6: 120
R7, R8: 2k2
SW1: SW_RESET
U1: ST485
U2: HYT271

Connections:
/DI: IC1.10 ((PCINT22/OC0A/AIN0)PD6), U1.4 (DI)
/LED1: D1.2 (K), IC1.23 ((PCINT8/ADC0)PC0)
/LED2: D2.2 (K), IC1.24 ((PCINT9/ADC1)PC1)
/MISO: IC1.16 ((PCINT4/MISO)PB4), P1.9
/MOSI: IC1.15 ((PCINT3/OC2/MOSI)PB3), P1.1
/RESET: IC1.29 ((PCINT14/~RESET~)PC6), P1.5, R3.1, SW1.1
/RX: IC1.30 ((PCINT16/RXD)PD0), P2.3
/SCK: IC1.17 ((PCINT5/SCK)PB5), P1.7
/SCL: IC1.28 ((PCINT14/SCL/ADC5)PC5), R8.1, U2.4 (SCL)
/SDA: IC1.27 ((PCINT12/SDA/ADC4)PC4), R7.1, U2.1 (SDA)
/TX: IC1.31 ((PCINT17/TXD)PD1), P2.2
/za: C5.1, J1.1, R4.2, U1.6 (A)
/zb: J1.2, R5.1, R6.1, U1.7 (B)
GND: C1.1, C2.1, C3.2, C4.2, C6.2, IC1.3 (GND), IC1.5 (GND), IC1.21 (GND), J1.7, J1.8, J1.9 (SHIELD), P1.6, P1.8, P1.10, P2.1, R5.2, SW1.2, U1.5 (GND), U2.2 (GND)
unnamed: D1.1 (A), R1.1
unnamed: C5.2, R6.2
unnamed: D2.1 (A), R2.1
VCC: C1.2, C2.2, C3.1, C4.1, C6.1, IC1.4 (VCC), IC1.6 (VCC), IC1.18 (AVCC), J1.4, J1.5, P1.2, P2.4, R1.2, R2.2, R3.2, R4.1, R7.2, R8.2, U1.2 (nRE), U1.3 (DE), U1.8 (VCC), U2.3 (VCC)

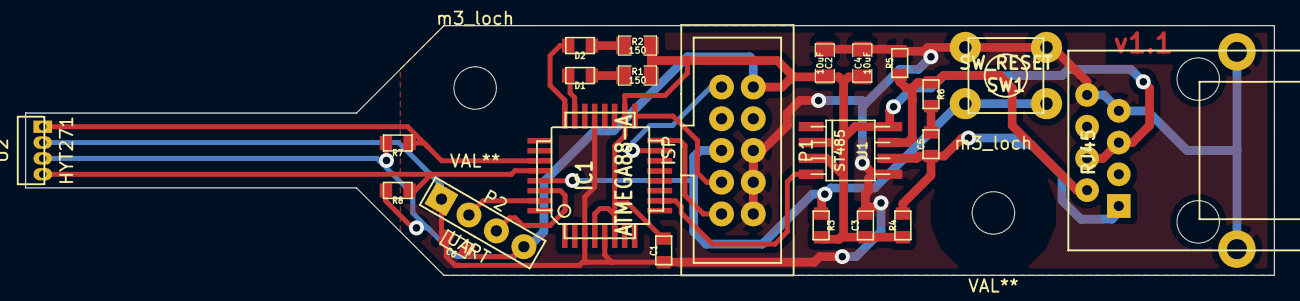
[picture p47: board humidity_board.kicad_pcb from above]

Board: 2 copper layers, 100.0 x 20.0 mm, 25 parts (0 on the bottom side), 18 nets.

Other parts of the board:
m3_loch, m3_loch#2: VAL**; m3_loch

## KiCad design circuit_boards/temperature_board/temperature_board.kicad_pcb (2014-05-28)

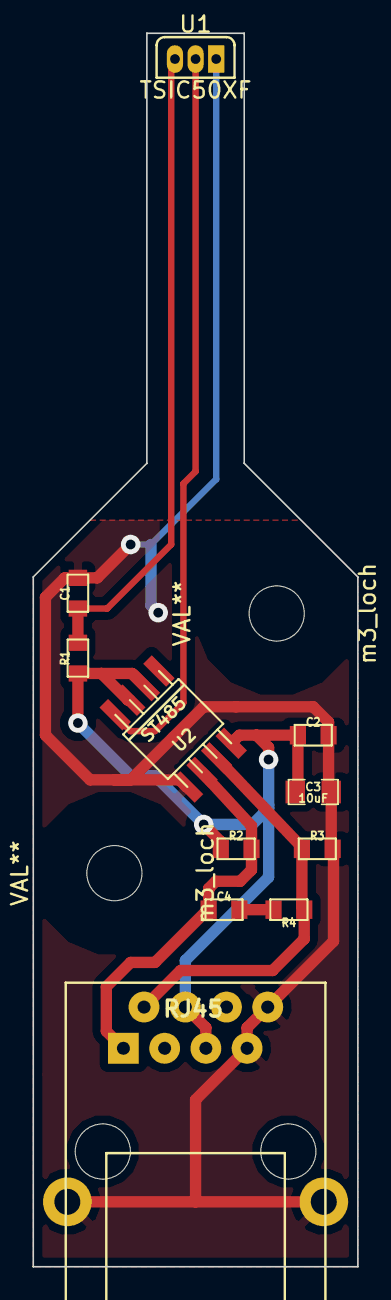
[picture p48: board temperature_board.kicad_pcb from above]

Board: 2 copper layers, 20.0 x 76.0 mm, 13 parts (0 on the bottom side), 7 nets.

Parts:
C1, C2, C4: 100nF; SM0603_big
C3: 10uF; SM0805_big
J1: RJ45; RJ45_8P8_simple
R1: 220; SM0603_big
R2, R3: 22k; SM0603_big
R4: 120; SM0603_big
U1: TSIC50XF; Tsic_TO92
U2: ST485; st485
m3_loch, m3_loch#2: VAL**; m3_loch

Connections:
/za: C4.1, J1.1, R2.2, U2.6
/zb: J1.2, R3.1, R4.1, U2.7
GND: C1.2, C2.2, C3.2, J1.7, J1.8, J1.9, R3.2, U1.1, U2.5
unnamed: C4.2, R4.2
unnamed: U1.2, U2.4
unnamed: C1.1, R1.2, U1.3
VCC: C2.1, C3.1, J1.4, J1.5, R1.1, R2.1, U2.2, U2.3, U2.8

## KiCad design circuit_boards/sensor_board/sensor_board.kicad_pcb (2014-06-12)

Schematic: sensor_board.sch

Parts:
C1, C23, C24: 10u
C2, C7, C8, C9, C10, C11, C12, C13, C14, C15, C16, C17, C18, C19, C20, C21, C22, C25, C26, C27, C28, C29, C30, C31, C32: 100n
C3, C4: 22p
C5: 330nF
C6: 100nF
D1: LED1
D2: LED2
D3: LED3
D4: LED4
D5: LED_POW
IC1: ATMEGA88A-A; TQFP32
J1: RJ45_8P8C_8FACH
K1: pow_sel
P1: UART
P2: Shield
P3: i2c_pow
P4: i2c_chain
P5: 12Vin
P6: HOHLBUCHSE
P7: Vccin
P8: ISP
P9: 5Vin
R1, R9: 10k
R2, R3, R4, R5, R8: 150
R6, R7: 2k2
R10, R11, R12, R13, R14, R15, R16, R17, R22, R23, R24, R25, R26, R27, R28, R29: 22k
R18, R19, R20, R21, R30, R31, R32, R33: 120
R34: 0
SW1: SW1
SW2: SCHALTER_2POL
SW3: SW_RESET
U1: LM7805
U2, U3, U4, U5, U6, U7, U8, U9: ST485
X1: 20MHz

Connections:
+12V: C5.1, P5.2 (PM), P6.1, U1.1
/LED1: D1.2 (K), IC1.14 ((PCINT2/OC1B/~SS~)PB2)
/LED2: D2.2 (K), IC1.13 ((PCINT1/OC1A)PB1)
/LED3: D3.2 (K), IC1.12 ((PCINT0/CLKO/ICP1)PB0)
/LED4: D4.2 (K), IC1.11 ((PCINT23/AIN1)PD7)
/MISO: IC1.16 ((PCINT4/MISO)PB4), P8.9
/MOSI: IC1.15 ((PCINT3/OC2A/MOSI)PB3), P8.1
/RESET: IC1.29 ((PCINT14/~RESET~)PC6), P8.5, R9.2, SW3.1
/RX: IC1.30 ((PCINT16/RXD)PD0), P1.2
/SCK: IC1.17 ((PCINT5/SCK)PB5), P8.7
/SCL: IC1.28 ((PCINT14/SCL/ADC5)PC5), P3.2, P4.2, SW2.1
/SDA: IC1.27 ((PCINT12/SDA/ADC4)PC4), P3.4, P4.4, SW2.2
/SW1: IC1.10 ((PCINT22/OC0A/AIN0)PD6), R1.1, SW1.1
/TX: IC1.31 ((PCINT17/TXD)PD1), P1.3
/Vi2c: K1.1, P3.5, P3.6, P4.5, P4.6
/Vreg: C6.1, K1.3, P9.2 (PM), U1.3
/XTAL1: C3.2, IC1.7 ((PCINT6/XTAL1/TOSC1)PB6), X1.2
/XTAL2: C4.2, IC1.8 ((PCINT7/XTAL2/TOSC2)PB7), X1.1
/ZAC_01: IC1.23 ((PCINT8/ADC0)PC0), U2.1 (RO)
/ZAC_02: IC1.24 ((PCINT9/ADC1)PC1), U3.1 (RO)
/ZAC_03: IC1.25 ((PCINT10/ADC2)PC2), U4.1 (RO)
/ZAC_04: IC1.26 ((PCINT11/ADC3)PC3), U5.1 (RO)
/ZAC_05: IC1.32 ((PCINT18/INT0)PD2), U6.1 (RO)
/ZAC_06: IC1.1 ((PCINT19/OC2B/INT1)PD3), U7.1 (RO)
/ZAC_07: IC1.2 ((PCINT20/XCK/T0)PD4), U8.1 (RO)
/ZAC_08: IC1.9 ((PCINT21/OC0B/T1)PD5), U9.1 (RO)
/z1a: C7.1, J1.a1, R10.2, U2.6 (A)
/z1b: J1.a2, R14.1, R18.1, U2.7 (B)
/z2a: C8.1, J1.b1, R11.2, U3.6 (A)
/z2b: J1.b2, R15.1, R19.1, U3.7 (B)
/z3a: C9.1, J1.c1, R12.2, U4.6 (A)
/z3b: J1.c2, R16.1, R20.1, U4.7 (B)
/z4a: C10.1, J1.d1, R13.2, U5.6 (A)
/z4b: J1.d2, R17.1, R21.1, U5.7 (B)
/z5a: C11.1, J1.e1, R22.2, U6.6 (A)
/z5b: J1.e2, R26.1, R30.1, U6.7 (B)
/z6a: C12.1, J1.f1, R23.2, U7.6 (A)
/z6b: J1.f2, R27.1, R31.1, U7.7 (B)
/z7a: C13.1, J1.g1, R24.2, U8.6 (A)
/z7b: J1.g2, R28.1, R32.1, U8.7 (B)
/z8a: C14.1, J1.h1, R25.2, U9.6 (A)
/z8b: J1.h2, R29.1, R33.1, U9.7 (B)
GND: C1.2, C2.2, C3.1, C4.1, C5.2, C6.2, C15.2, C16.2, C17.2, C18.2, C19.2, C20.2, C21.2, C22.2, C23.2, C24.2, C25.2, C26.2, C27.2, C28.2, C29.2, C30.2, C31.2, C32.2, D5.2 (K), IC1.3 (GND), IC1.5 (GND), IC1.21 (GND), J1.a7, J1.a8, J1.b7, J1.b8, J1.c7, J1.c8, J1.d7, J1.d8, J1.e7, J1.e8, J1.f7, J1.f8, J1.g7, J1.g8, J1.h7, J1.h8, J1.s, P1.4, P3.1, P3.3, P4.1, P4.3, P5.1, P6.3, P7.1, P8.6, P8.8, P8.10, P9.1, R1.2, R14.2, R15.2, R16.2, R17.2, R26.2, R27.2, R28.2, R29.2, R34.2, SW3.2, U1.2, U2.2 (nRE), U2.3 (DE), U2.5 (GND), U3.2 (nRE), U3.3 (DE), U3.5 (GND), U4.2 (nRE), U4.3 (DE), U4.5 (GND), U5.2 (nRE), U5.3 (DE), U5.5 (GND), U6.2 (nRE), U6.3 (DE), U6.5 (GND), U7.2 (nRE), U7.3 (DE), U7.5 (GND), U8.2 (nRE), U8.3 (DE), U8.5 (GND), U9.2 (nRE), U9.3 (DE), U9.5 (GND)
unnamed: R7.2, SW2.4
unnamed: R6.2, SW2.3
unnamed: P2.1, R34.1
unnamed: C14.2, R33.2
unnamed: C12.2, R31.2
unnamed: C13.2, R32.2
unnamed: D4.1 (A), R5.1
unnamed: D3.1 (A), R4.1
unnamed: D5.1 (A), R8.2
unnamed: D2.1 (A), R3.1
unnamed: D1.1 (A), R2.1
unnamed: C7.2, R18.2
unnamed: C9.2, R20.2
unnamed: C10.2, R21.2
unnamed: C11.2, R30.2
unnamed: C8.2, R19.2
VCC: C1.1, C2.1, C15.1, C16.1, C17.1, C18.1, C19.1, C20.1, C21.1, C22.1, C23.1, C24.1, C25.1, C26.1, C27.1, C28.1, C29.1, C30.1, C31.1, C32.1, IC1.4 (VCC), IC1.6 (VCC), IC1.18 (AVCC), J1.a4, J1.a5, J1.b4, J1.b5, J1.c4, J1.c5, J1.d4, J1.d5, J1.e4, J1.e5, J1.f4, J1.f5, J1.g4, J1.g5, J1.h4, J1.h5, K1.2 (PM), P1.1, P7.2 (PM), P8.2, R2.2, R3.2, R4.2, R5.2, R6.1, R7.1, R8.1, R9.1, R10.1, R11.1, R12.1, R13.1, R22.1, R23.1, R24.1, R25.1, SW1.2, U2.8 (VCC), U3.8 (VCC), U4.8 (VCC), U5.8 (VCC), U6.8 (VCC), U7.8 (VCC), U8.8 (VCC), U9.8 (VCC)

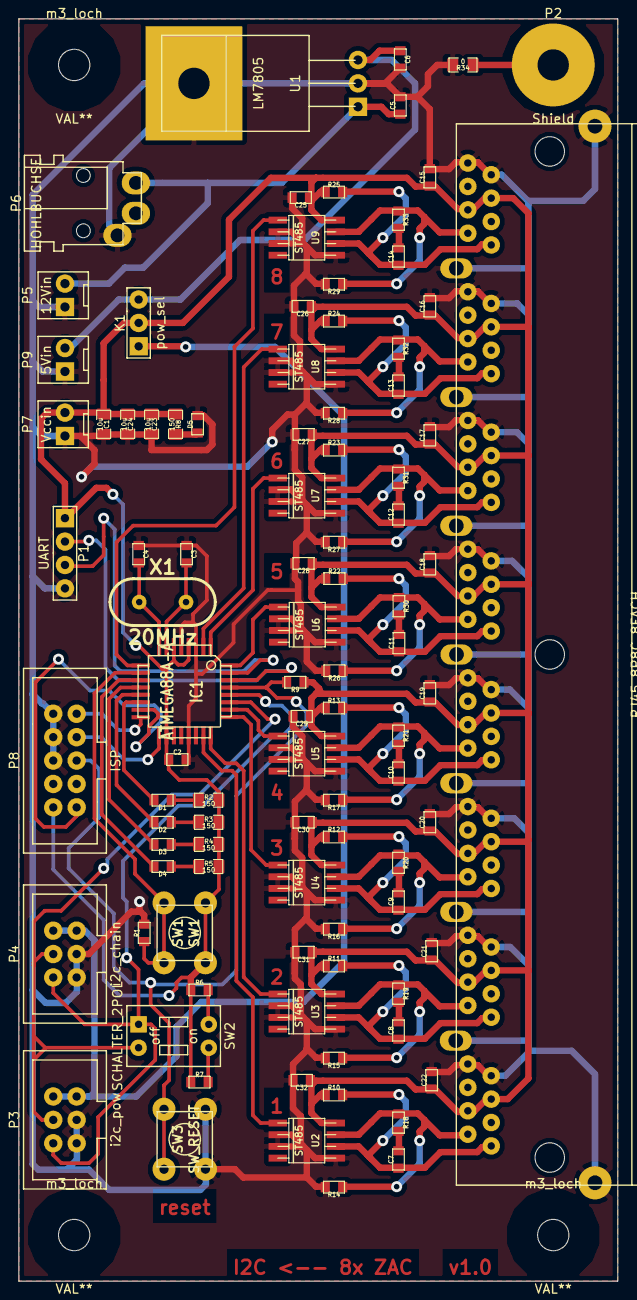
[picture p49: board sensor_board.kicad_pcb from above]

Board: 2 copper layers, 65.0 x 137.0 mm, 99 parts (0 on the bottom side), 60 nets.

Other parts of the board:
m3_loch, m3_loch#2, m3_loch#3: VAL**; m3_loch

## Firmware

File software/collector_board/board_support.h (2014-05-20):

#ifndef BOARD_SUPPORT_H
#define BOARD_SUPPORT_H

#include <avr/io.h>


// LEDs:
#define LED1 PB2
#define LED2 PB1
#define LED3 PB0
#define LED4 PD7

#define LED1_PORT PORTB
#define LED2_PORT PORTB
#define LED3_PORT PORTB
#define LED4_PORT PORTD

#define LED1_DDR DDRB
#define LED2_DDR DDRB
#define LED3_DDR DDRB
#define LED4_DDR DDRD

// SWITCHES:
#define SW1 PD6
#define SW1_PORT PORTD
#define SW1_DDR DDRD


#endif

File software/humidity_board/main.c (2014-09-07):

#include <avr/io.h>
#include <avr/interrupt.h>
#include <util/delay.h>
#include "usart.h"
#define DELAY_AFTER_MR_MS 55
#define DELAY_BEFORE_DF_US 20
#define START_TIMER TCCR0B |= (1<< CS01);// 8mHz/8
//#define START_TIMER TCCR0B |= (1<< CS01 | 1<<CS00);// 8mHz/64  
//#define START_TIMER TCCR0B |= (1<< CS02 | 1<<CS00);// 8mHz/1024
#define STOP_TIMER TCCR0B = 0; //disable timer
#define SLA 0x28
#define CMODE 7
#define STALE 6
#define TSTART_US 64
#define TLONG_US 96
#define TSHORT_US 32
// the using polynomial is 100110001
// the 9. bit is implicit in computation 
#define CRC8 49
// set debug module
// XXX using debug module will influent the frequence of the sending data via ZAC wire protocol because of printf, so the connected collection board will not alreadys get sent data
//#define DEBUG

uint8_t capH=0;
uint8_t capL=0;
uint8_t tempH=0;
uint8_t tempL=0;
uint8_t crc=0;
#ifdef DEBUG
uint8_t crc_verified=0xff;
uint8_t cap=0xff;
uint8_t temp=0xff;
#endif
int8_t counter_sent = 0;
volatile int8_t sending = 0;

uint8_t waitUntilFinished(uint8_t status){
  while(!(TWCR & (1 << TWINT))){
    // FIXME do break 
    asm("nop");
     //printf("TWSR is %x\n\r", TWSR);
    // sorry, i'm busy wating!!
  }
  if (TWSR == status){
    return 1;  
  }
  return 0;
}

void  requestMeasuring(){
#ifdef DEBUG
  printf("Measurement Request\n\r");
#endif
  /* Start condition*/
  TWCR = ((1 << TWINT) | (1 << TWSTA) | (1 << TWEN));
  if (!waitUntilFinished(0x8)){
    return;  
  }
  /* SLA + W (bit 0)*/
  TWDR = (SLA << 1);
  TWCR = ((1 << TWINT) | (1 << TWEN));
  /* TWSR = 0x18 means SLA+W has been transmitted; ACK has been received*/
  if (!waitUntilFinished(0x18)){
    return;
  }
  /* Stop condition*/
  TWCR = ((1 << TWINT) | (1 << TWSTO) | (1 << TWEN));
#ifdef DEBUG
  printf("Required\n\r");
#endif
}

uint8_t readByte(uint8_t ack){
  TWCR = ((1 << TWINT) | (ack << TWEA) | (1 << TWEN));
  // TWSR = 0x50 means Data byte has been received; ACK has been returned
  if (!waitUntilFinished(0x50)){
    return 0;
  }
  return TWDR;
}

void fetchData(){
#ifdef DEBUG
  printf("Data Fetch\n\r");
#endif
  /* Start condition*/
  TWCR = ((1 << TWINT) | (1 << TWSTA) | (1 << TWEN));
  if (!waitUntilFinished(0x8)){
    return;  
  }
  /* SLA + R (bit 1)*/
  TWDR = (SLA << 1) | (1 << 0);
  TWCR = ((1 << TWINT) | (1 << TWEN));
  /* TWSR = 0x40 means SLA+R has been transmitted; ACK has been received*/
  if (!waitUntilFinished(0x40)){
    return;
  }

  capH = readByte(1);
  capL = readByte(1);
  tempH = readByte(1);
  tempL = readByte(0);

  /* Stop condition*/
  TWCR = ((1 << TWINT) | (1 << TWSTO) | (1 << TWEN));
#ifdef DEBUG
  printf("Fetched\n\r");
#endif
}

void computeByteCRC(uint8_t *result, uint8_t byte) {
  int8_t index = 7;
  for(index=7; index >= 0; index--){
    if(*result & (1<<7)){
      *result = *result << 1;
      *result |= ((byte >> index) & 1);
      *result ^= CRC8;
    } else  {
      *result = *result << 1;
      *result |= ((byte >> index) & 1);
    }
  }
}

void computeCRC(){
  crc = capH;
  computeByteCRC(&crc, capL);
  computeByteCRC(&crc, tempH);
  computeByteCRC(&crc, tempL);
  computeByteCRC(&crc, 0);
}

#ifdef DEBUG
void verifyCRC(){
  crc_verified = capH;
  computeByteCRC(&crc_verified, capL);
  computeByteCRC(&crc_verified, tempH);
  computeByteCRC(&crc_verified, tempL);
  computeByteCRC(&crc_verified, crc);
  printf("Verified Result is %x\n\r", crc_verified);
}
#endif

// interrupt handler for output compare register A
ISR(TIMER0_COMPA_vect){
  if (counter_sent >=0){
    if(counter_sent < 79){
      if(counter_sent%2 == 0){
        if(capH & (1<<7)){
        // send 1
          OCR0A = TSHORT_US;
        }else{
        // send 0
          OCR0A = TLONG_US;
        }
      } else { 
        if(capH & (1<<7)){
        // send 1
          OCR0A = TLONG_US;
        }else{
        // send 0
          OCR0A = TSHORT_US;
        }
        // Roll data 
        crc = crc << 1;
        // use "rol" to shift the other two bits with carry
        asm("rol %0" : "=r" (tempL) : "0" (tempL));
        asm("rol %0" : "=r" (tempH) : "0" (tempH));
        asm("rol %0" : "=r" (capL) : "0" (capL));
        asm("rol %0" : "=r" (capH) : "0" (capH));
      }
    } else{
      STOP_TIMER
      // Disable timer output compare match A interrupt when sending bits
      TIMSK0 &= ~( 1 << OCIE0A ); 
      // Disable clear timer TCNT0 on compare match register A: OCR0A
      TCCR0A &= ~(1 << WGM01); 
      sending = 0;
    }
  }
  counter_sent++;
}

void convertToZAC(){
#ifdef DEBUG
  printf("Start sending: capH = %x\n\r", capH);
#endif
  // Set OC0A at the beginning
  TCCR0A |= ((1 << COM0A0) | (1 << COM0A1)); 
  TCCR0B |= (1 << FOC0A);

  // prepare for sending START bit
  TCNT0 = 0;
  OCR0A = TSTART_US;
  counter_sent = -2;

	// Enable timer output compare match A interrupt when sending bits
  TIMSK0 |= ( 1 << OCIE0A ); 
  // Enable clear timer TCNT0 on compare match register A: OCR0A
  TCCR0A |= (1 << WGM01); 
  // Enable Toggle OC0A on compare match
  TCCR0A &= ~(1 << COM0A1); 
  TCCR0A |= (1 << COM0A0); 
  // Flag of sending
  sending = 1;
  // Timer init 
  START_TIMER 
  while(sending){
    // busy wating until finishing sending
    asm("nop");
  }
  // Set OC0A at the end 
  TCCR0A |= ((1 << COM0A0) | (1 << COM0A1)); 
  TCCR0B |= (1 << FOC0A);
}

void loop(){
  uint8_t counter=0;
  requestMeasuring();
  // measurement will be ready after 50...60ms (this value was aquired by experimental meassurement).
  _delay_ms(DELAY_AFTER_MR_MS);
  counter=0;
  do{
    _delay_us(DELAY_BEFORE_DF_US);
    counter ++;
    fetchData();
    /* Do datafetch until the stale bit is 0 
     * If more than 100 times, give up */
  }while((capH & ( (1 << STALE))) && counter <100 );
#ifdef DEBUG
  printf("Fetching counter is %d\n\r", counter);
#endif
  // remove status bits
  capH = capH & 0x3f;
  
  computeCRC();
#ifdef DEBUG
  printf("capH = %x\n\r", capH);
  printf("capL = %x\n\r", capL);
  printf("tempH = %x\n\r", tempH);
  printf("tempL = %x\n\r", tempL);
  printf("crc=%x\n\r", crc);

  // converted roughly for test
  cap = ((capH*3) >> 1) + (capH >>4);
  temp = (tempH >> 1) + (tempH >> 3) + (tempH >> 6) ;

  printf("converted cap = %u\n\r", cap);
  printf("converted temp = %u - 40 = %d\n\r", temp, temp-40);

  verifyCRC();
#endif

  convertToZAC();
}

int main (void)
{
	static FILE usart_stdout = FDEV_SETUP_STREAM( mputc, 0, _FDEV_SETUP_WRITE);
	stdout = &usart_stdout;

	uart_init();
	sei();

  // init registers for i2c
  // Fscl = CPU clock frequency/(16 + 2(TWBR))
  // Set Fscl 50 kHz
  // TWBR = 72; 
  // Set Fscl 100 kHz
  TWBR = 32; 
  // Set Fscl 200 kHz
  // TWBR = 12; 

  printf("Start\n\r");
	DDRD |= (1<<PD6);
  _delay_ms(1000);
  // Set internal pull-ups
  PORTC |= (1<<PC4);
  PORTC |= (1<<PC5);

  while(1){
    loop();
  }
}

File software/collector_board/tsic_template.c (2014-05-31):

#undef TEMPL_TMR_OVF_VECT
#undef TEMPL_PCINT_VECT
#undef TEMPL_TCCRA
#undef TEMPL_TCCRB
#undef TEMPL_PCMSK
#undef TEMPL_TCNT
#undef TEMPL_PIN
#undef TEMPL_TCRIT
#undef TEMPL_TVAL
#undef TEMPL_LOWTIME
#undef TEMPL_SENSOR_PIN
#undef TEMPL_BYTE_ARRAY
#undef TEMPL_START_MEASSURE
#undef TEMPL_STOP_MEASSURE
#undef TEMPL_PCIF
#undef TEMPL_PCIE
#undef TEMPL_START_TIMER
#undef TEMPL_INIT
#undef TEMPL_TIMSK // Timer/Counter Interrupt Mask Rigister
#undef TEMPL_TIMSK_TOIE // Timer/Counter Overflow Interrupt Enable bit
#undef TEMPL_N_SENSOR_PIN
#if BANK == 1
	uint8_t lowtime1;
	uint8_t bytearr_bank1[5];
	uint8_t sensor_pin_mask1 = (1<<PC0);
	uint8_t nsensor_pin_mask1 = ~(1<<PC0);
	#define TEMPL_TMR_OVF_VECT TIMER2_OVF_vect
	#define TEMPL_PCINT_VECT PCINT1_vect
	#define TEMPL_TCCRA TCCR2A
	#define TEMPL_TCCRB TCCR2B
	#define TEMPL_PCMSK PCMSK1
	#define TEMPL_TCNT TCNT2
	#define TEMPL_PIN PINC
	#define TEMPL_TCRIT OCR2A
	#define TEMPL_TVAL OCR2B
	#define TEMPL_LOWTIME lowtime1
	#define TEMPL_SENSOR_PIN sensor_pin_mask1
	#define TEMPL_N_SENSOR_PIN nsensor_pin_mask1
	#define TEMPL_BYTE_ARRAY bytearr_bank1
	#define TEMPL_START_MEASSURE meassure_start_bank1
	#define TEMPL_STOP_MEASSURE meassure_stop_bank1
	#define TEMPL_PCIF PCIF1
  #define TEMPL_PCIE PCIE1 //enable interrupt for PCINT[14...8]

	#define TEMPL_START_TIMER TEMPL_TCCRB = (1<<CS22)

  #define TEMPL_INIT int_init1
  #define TEMPL_TIMSK TIMSK2
  #define TEMPL_TIMSK_TOIE TOIE2
#elif BANK == 2
	uint8_t lowtime2;
	uint8_t bytearr_bank2[5];
	uint8_t sensor_pin_mask2 = (1<<PD2);
	uint8_t nsensor_pin_mask2 = ~(1<<PD2);
	#define TEMPL_TMR_OVF_VECT TIMER0_OVF_vect
	#define TEMPL_PCINT_VECT PCINT2_vect
	#define TEMPL_TCCRA TCCR0A
	#define TEMPL_TCCRB TCCR0B
	#define TEMPL_PCMSK PCMSK2
	#define TEMPL_TCNT TCNT0
	#define TEMPL_PIN PIND
	#define TEMPL_TCRIT OCR0A
	#define TEMPL_TVAL OCR0B
	#define TEMPL_LOWTIME lowtime2
	#define TEMPL_SENSOR_PIN sensor_pin_mask2
	#define TEMPL_N_SENSOR_PIN nsensor_pin_mask2
	#define TEMPL_BYTE_ARRAY bytearr_bank2
	#define TEMPL_START_MEASSURE meassure_start_bank2
	#define TEMPL_STOP_MEASSURE meassure_stop_bank2
	#define TEMPL_PCIF PCIF2
  #define TEMPL_PCIE PCIE2 //enable interrupt for PCINT[7...0]

	#define TEMPL_START_TIMER TEMPL_TCCRB = (1<<CS01) | (1<<CS00)

  #define TEMPL_INIT int_init2
  #define TEMPL_TIMSK TIMSK0
  #define TEMPL_TIMSK_TOIE TOIE0
#else

#endif

void TEMPL_INIT (){
	// enable interrupt will be done when starting measurement
	PCICR |= ( 1 << TEMPL_PCIE ); //Pin change interrupt enable
	// enable timer overflow interrupt
	TEMPL_TIMSK = ( 1 << TEMPL_TIMSK_TOIE ); 
  // Timer init (reset to default)
	TEMPL_TCCRA = 0;
	TEMPL_TCCRB = 0;
}

// Timer overflow interrupt handler
ISR(TEMPL_TMR_OVF_VECT){
	TEMPL_TCCRB = 0; //disable timer
	// we use the fact, that TSIC always sends 5 zeroes at the beginning
	// to determine, if the transmission was complete
	// as it might happen, that we start meassuring just before the
	// second start bit. We then have to wait for the next transmission
  //uint8_t b = !(TEMPL_BYTE_ARRAY [2] & (1<<2));
  //printf("b: 0x%x\n\r",b);
#ifdef DEBUG
	printf ("%x %x %x %d\n\r", TEMPL_BYTE_ARRAY [2], TEMPL_BYTE_ARRAY [1], TEMPL_BYTE_ARRAY [0], s);
#endif
	if (!(TEMPL_BYTE_ARRAY [2] & (1<<2)) || !(TEMPL_BYTE_ARRAY [4] & (1<<7))){
		// we have seen a start bit AND are finished with transmission
		// => stop measurement
		// disable interrupt for this pin
		// -> unmask:
		TEMPL_PCMSK &= TEMPL_N_SENSOR_PIN;
		// TODO: check, if we have to clear possibly arrived interrupts
		// this this would be done by writing 1 to the corresponding bit:
		// PCIFR |= (1<< PCIF1);

	}else{
		// we will receive the rest of the data in the next iteration
		// hence we have to clean up the buffer, as we have to have a defined state
		// to distinguish between humidity and temperature sensor
		TEMPL_BYTE_ARRAY [4] = 0xff;
		TEMPL_BYTE_ARRAY [3] = 0xff;
		TEMPL_BYTE_ARRAY [2] = 0xff;
		TEMPL_BYTE_ARRAY [1] = 0xff;
		TEMPL_BYTE_ARRAY [0] = 0xff;
		// we also have to set the timer value to initial value
		// this has to be done for spike detection to work correctly
		TEMPL_TCNT = 0xff;
		// low time mightalso be 0xff -> this might cause problems
		// if transmission starts again. so set it to default state 0:
		TEMPL_LOWTIME = 0;
	}
}

// Interrupt handler
// IDEA: use OCRnA/B for TEMPL_TCRIT / TEMPL_TVAL storage to reduce stack usage
ISR(TEMPL_PCINT_VECT){
  icount++;
	// start timer 2: enable with prescaler 64
	// the order AND position of the following 3 instructions
	// is highly important for propper timing
	// The timer should be started as soon as possible
	// After that the timer value should be reset to 0 as soon as possible too
	TEMPL_START_TIMER;
  // Read timer 2
	TEMPL_TVAL = TEMPL_TCNT;
  // Reset timer 2
	TEMPL_TCNT = 0;
  
#ifdef SPIKEDETECT
	// this should filter out vibrations on the wire
	// FIXME: check if we need this. I was not able to construct
	// a situation, where this was called in a lab environment.
	// But maybe with long wires we might have spikes.
	// We need to check, if timer is already running,
	// as this might be the first interrupt, where
	// TEMPL_TVAL is 0 by default.
	if (TEMPL_TVAL < 2){
		//printf("INSTABILITY!\n\r");
		return;
	}
#endif

	//TEMPL_TCCRB = (1<<CS22);
	if(TEMPL_PIN & TEMPL_SENSOR_PIN){
#ifdef DEBUG
		timesr[cr] = TEMPL_TVAL;
		cr++;
#endif
		// PC0 is 1 -> rising edge
		// this is the time, the signal was low:
		TEMPL_LOWTIME = TEMPL_TVAL;
		// TODO: Idea:
		// Try to directly use 16 bis or 32 bit integers. this might reduce
		// stack and register overhead
		if (TEMPL_TCRIT != 0xff){
			// here we receive a TEMPL_BYTE_ARRAY.
			// we now know, that we have received a start bit in the past
			// shift all 3 TEMPL_BYTE_ARRAYs to the left:
			// shift first TEMPL_BYTE_ARRAY -> carry flag is the msb
			TEMPL_BYTE_ARRAY [4] = (TEMPL_BYTE_ARRAY [4] << 1);
			// use "rol" to shift the other two bits with carry
			asm("rol %0" : "=r" (TEMPL_BYTE_ARRAY [3]) : "0" (TEMPL_BYTE_ARRAY [3]));
			asm("rol %0" : "=r" (TEMPL_BYTE_ARRAY [2]) : "0" (TEMPL_BYTE_ARRAY [2]));
			asm("rol %0" : "=r" (TEMPL_BYTE_ARRAY [1]) : "0" (TEMPL_BYTE_ARRAY [1]));
			asm("rol %0" : "=r" (TEMPL_BYTE_ARRAY [0]) : "0" (TEMPL_BYTE_ARRAY [0]));
			// now we write the received bit:
			// if this (rising) edge happened before the critical time,
			// we extracted from the start bit, we are dealing with a '1',
			// else with a '0'
			TEMPL_BYTE_ARRAY [4] = TEMPL_BYTE_ARRAY [4] ^ (TEMPL_TVAL < TEMPL_TCRIT);
		}
	}else{
#ifdef DEBUG
		times[cf] = TEMPL_TVAL;
		cf++;
#endif
		// PC0 is 0 -> falling edge
		// we check for a start bit:
		// A start bit should have a duty cycle of 50%
		// We also accept bits as start bits within a small mergin
		// If we have detected a start bit, we use the high time of the
		// bit as the critical time TEMPL_TCRIT
		if(TEMPL_LOWTIME>TEMPL_TVAL){
			if(TEMPL_LOWTIME-TEMPL_TVAL < 3){
				TEMPL_TCRIT = TEMPL_TVAL;
#ifdef DEBUG
				s++;
				tcritb = TEMPL_LOWTIME;
				tcrita = TEMPL_TVAL;
#endif
			}
		}else{
			if(TEMPL_TVAL-TEMPL_LOWTIME < 3){
				TEMPL_TCRIT = TEMPL_TVAL;
#ifdef DEBUG
				s++;
				tcritb = TEMPL_LOWTIME;
				tcrita = TEMPL_TVAL;
#endif
			}
		}
	}
}
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

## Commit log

2014-03-01 datasheet for sensor
2014-03-02 feuchtigkeit sensoren data :
2014-03-02 new sensor
2014-03-07 arduino zeug
2014-03-20 inline assembler mod
2014-03-22 add temperature board schematic and kicad library for TSic 50xF and ST485
    [temperature_board.sch]
2014-03-22 pin number of hyt271
2014-03-22 add HYT271 library and humidity board schematic (TODO problem with I2C)
    [humidity_board.sch]
2014-03-22 sensor board
    [sensor_board.sch]
2014-03-23 sendor_board bigger controller
    [sensor_board.sch]
2014-03-24 complete humidity board schematic
    [humidity_board.sch]
2014-03-24 sensor board: led fix
    [sensor_board.sch]
2014-03-30 sensor_board updated
    [sensor_board.sch]
2014-03-30 templating + 2 sensors after another
2014-03-31 wrote simple worst case ecexution time analyzer
2014-03-31 modified test case
2014-04-11 pollin eval board datasheet added
    [temperature_board.sch]
2014-04-15 hardware + bestellungen
    [humidity_board.sch, main.sch, sensor_board.sch, temperature_board.sch]
2014-04-25 rj45 8 port changed pin order
2014-04-26 schematic sensor board
    [sensor_board.sch]
2014-04-27 7805 schematic library
    [sensor_board.sch]
2014-04-27 board started
    [sensor_board.kicad_pcb, sensor_board.sch]
2014-04-27 modify sensor board schematik
    [humidity_board.sch, temperature_board.sch]
2014-04-27 sensor board pcb routing started
    [sensor_board.kicad_pcb, sensor_board.sch]
2014-04-28 sensor_board: all connected
    [sensor_board.kicad_pcb, sensor_board.sch]
2014-04-28 zones added
    [sensor_board.kicad_pcb]
2014-04-28 comments in schematics
    [humidity_board.sch, temperature_board.sch]
2014-04-28 fixed unconnected zac wire
    [sensor_board.kicad_pcb, sensor_board.sch]
2014-04-29 modify again
    [humidity_board.sch]
2014-04-29 begin with pcb
    [humidity_board.sch, temperature_board.sch]
2014-04-29 add netlist and pcb
    [humidity_board.kicad_pcb, humidity_board.sch, temperature_board.kicad_pcb, temperature_board.sch]
2014-04-30 sensor_board complete
    [sensor_board.kicad_pcb, sensor_board.sch]
2014-04-30 temperature board pcb finished
    [temperature_board.kicad_pcb]
2014-04-30 begin with humidity board pcb
    [humidity_board.kicad_pcb]
2014-04-30 add m3 schraube
    [humidity_board.kicad_pcb]
2014-05-01 humidity pcb finished
    [humidity_board.kicad_pcb, humidity_board.sch]
2014-05-01 TODO change sensor module
    [humidity_board.kicad_pcb]
2014-05-01 change sensor modules
    [humidity_board.kicad_pcb, temperature_board.kicad_pcb]
2014-05-06 sensor_board final version
    [sensor_board.kicad_pcb]
2014-05-06 sensor board smaller
    [sensor_board.kicad_pcb]
2014-05-06 change humidity
    [humidity_board.kicad_pcb, temperature_board.kicad_pcb]
2014-05-06 optimal temperature pcb
    [temperature_board.kicad_pcb]
2014-05-06 humidity smaller
    [humidity_board.kicad_pcb]
2014-05-06 humidity led pos + zones
    [humidity_board.kicad_pcb]
2014-05-07 finalized boards for production
    [humidity_board.kicad_pcb, humidity_board.sch, sensor_board.kicad_pcb, temperature_board.kicad_pcb]
2014-05-07 breakout boards + order
    [3x127_254_adapter.kicad_pcb, 3x127_254_adapter.sch, 4x127_254_adapter.kicad_pcb, 4x127_254_adapter.sch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]
2014-05-07 pcb for adaptor board
    [main.kicad_pcb]
2014-05-07 moved modules
    [3x127_254_adapter.kicad_pcb, 4x127_254_adapter.kicad_pcb, main.kicad_pcb, order.kicad_pcb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]
2014-05-07 moved again...
    [main.kicad_pcb, order.kicad_pcb]
2014-05-07 all boards
    [order2.kicad_pcb]
2014-05-07 2 humidity together
    [order2.kicad_pcb]
2014-05-07 humidity in place
    [order2.kicad_pcb]
2014-05-07 2 temp boards
    [order2.kicad_pcb]
2014-05-07 10 temp sensor work
    [order2.kicad_pcb]
2014-05-07 sensor board rotated
    [order2.kicad_pcb]
2014-05-08 order4 is plotting :)
    [order4_notent.kicad_pcb]
2014-05-08 gerber files
    [order4_notent-NPTH.drl, order4_notent.drl]
2014-05-20 software for collector board
2014-05-20 led blinks on connection state change
2014-05-26 added i2c pullups to humidity board
    [humidity_board.kicad_pcb, humidity_board.sch]
2014-05-28 for put all together
    [humidity_board.kicad_pcb, sensor_board.kicad_pcb, temperature_board.kicad_pcb]
2014-05-28 strange pcb is saved in temperature_board-append.kicad_pcb
    [temperature_board-append.kicad_pcb]
2014-05-28 finished but crash by plot gerb file
    [newOrder.kicad_pcb]
2014-05-28 3 humidity boards but just 19 temperature
    [humidity_board.kicad_pcb, temperature_board-append.kicad_pcb]
2014-05-28 3 humidity but 19 temperature
    [newOrder.kicad_pcb]
2014-05-28 23 temperature 2 humility
    [newOrder.kicad_pcb]
2014-05-28 finished and can be plot
    [newOrder.kicad_pcb]
2014-05-28 a little modification
    [humidity_board.kicad_pcb, newOrder.kicad_pcb, so8_breakout.kicad_pcb]
2014-05-28 collector board: twi state machine
    [newOrder.kicad_pcb]
2014-05-29 ethernet board i2c interface implemented
2014-05-31 i2c works quite stable for 1 board
2014-05-31 improve computing humility sensor data
2014-05-31 also for ethernet board
2014-05-31 fix hum temperature
2014-05-31 fixed temperature conversion 10000->100
2014-06-01 also for collection board
2014-06-01 moved collector board interface to separate file
2014-06-02 somehow works, but we lost sensor 8 during transmission
2014-06-02 fixed losing 8th sensor. (just did not receive enough data)
2014-06-03 collector board: config works
2014-06-04 collector board compiles
2014-06-07 function to print result to socket
2014-06-10 collector board is broken, somehow config save does not work
2014-06-12 fixed socket file aproach
2014-06-15 implemented twi led control
2014-06-15 implemented led cmd
2014-06-15 implemented LED cmd, changed socket and cmd handling alot, now buggy
2014-06-15 led fixes
2014-06-21 many images :)
    [temperature_board.sch]
2014-06-21 report schematic images
    [humidity_board.sch, sensor_board.sch, temperature_board.sch]
2014-06-26 config works for ethernet board
2014-07-09 buglist, cleanup, debugging enabled printf CHANGE BACK AFTER FIX
2014-07-10 improved db communication speed (replies) -> arduino library plugin for w5100 clear buffer support
2014-07-10 clear printf
2014-07-10 printf => putc
2014-07-20 report: collector board hardware description
2014-07-20 report: collector board complete
2014-09-05 all case versions, - chaos
    [adapter_finished_rounded_stl.stl, arduino_body.step, arduino_body.stl, arduino_case.stl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]
2014-09-05 removed irrelevant cases CAD files
    [arduino_case.stl, arduino_deckel.stl, collector_case.stl, collector_deckel.stl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]
2014-09-05 added solidworks file for hum and temp, but might be out of date. FIXME: stp and stl files needed for temperature and humidity cases
    [hum_base.SLDPRT, hum_cable-clamp.SLDPRT, hum_cable-clamp1.SLDPRT, hum_cable-clamp2.SLDPRT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]
2014-09-05 repository cleanup
    [3x127_254_adapter.kicad_pcb, 3x127_254_adapter.sch, 4x127_254_adapter.kicad_pcb, 4x127_254_adapter.sch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]
2014-09-07 review sensors part
2014-09-07 report: ethernet board software finished
2014-09-07 review temperature board
2014-09-07 write sth to humidity board
2014-09-10 report: pin picture reference
2014-09-12 images for boards + report appedix moved schematics
2014-09-13 reviewed until Ethernet board
2014-09-15 report: corrections until 3.3 collector board
2014-09-15 report: corrections until ethernet board
2014-09-15 remove orders
    [newOrder.kicad_pcb, order.kicad_pcb, order2.kicad_pcb, order3.kicad_pcb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]
